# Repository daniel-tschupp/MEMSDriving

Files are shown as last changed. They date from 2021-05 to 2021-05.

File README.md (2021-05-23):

# OCT MEMS Scanhead

As my second project in my master studies designed a 2d OCT MEMS Scanhead.

It contained three main tasks:
* Signal processing for drifing the MEMS
* Driver electronics design
* MCU Signal generation electronics design including Software

This repository contains the entier work including a documantaion in pdf format and the presentation as a video in german.

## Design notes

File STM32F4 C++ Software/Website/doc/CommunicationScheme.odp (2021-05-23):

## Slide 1

USB-C

Protocoll: json

UART

WiFi: TCP Socket

Protocoll: json

UART

Html5
Websockets

Host PC

Labview serial port

C++ serial port

Scanner PCB

FTDI

MCU

Host PC

Labview tcp-socket

C++ tcp-socket

Website

Proxy
Server

Scanner PCB

ESP8266
server
(Port:5001)

MCU

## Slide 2

Scheduler (FIFO)

Taskqueue possible entries:

Initialize system on startup

USB Task:
- Check command
- Check parameter ranges
- Configure system accordingly

Wifi Task:
- Check command
- Check parameter ranges
- Configure system accordingly

Realtime (Interrupts: asynchronous)

USB-USART:
Add character to USB buffer

ESP8266-USART:
Add character to Wifi buffer

Timer DAC: (sampling frequency)
Calculate and Update
DAC value

A-Scan-Trigger:
Count A-Scans

Timer Regular checks: (100ms)
Add USB task to tasklist
Add Wifi task to tasklist

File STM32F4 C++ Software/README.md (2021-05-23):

## Overview over Documentation:
*	[Prerequisits](#Prerequisites)
*	[Main structure](#MainStructure)
*	[Hardware](#Hardware)
*	[Signal Generation](#SignalGeneration)
*	[Communication](#Communication)

_Note: When this README.md file is displayed on GitLab, the images won't be displayed.
To see the whole file, please clone the repo and execute: "$doxygen doxyfile"
on tht cmd line. Then enter "$firefox doxygen/html/index.html" 
Make sure you met the prerequisits._
 
---

## <a name="Prerequisites">Prerequisits to work on this Project:</a>

---

For Linux:
* git
* Atollic True Studio
* CubeMX
* doxygen (Download & compile the latest version from: https://gitlab.com/pages/doxygen/tree/master )
* graphviz

For Windows:
* git
* Atollic True Studio or Keil uVision
* CubeMX
* doxygen Frontend
* graphviz that works with doxygen frontend
* cygwin with doxygen and graphviz

---

## <a name="MainStructure">Main structure of the software:</a>

---

The Software is build up into 2 parts:
* Foreground (Time critical)
* Background (still realtime but not time critical)

MEMSScanner
!
### Foreground
The foreground only consists of interrupt service routins. The main part is the signal generation for the MEMS mirrors (Timer 13). 
But there are also some timer interrupts for event generation for the background part of the software.

Actual tasks of the foreground:
*	x-axis and y-axis signal generation (timer 13)
*	a-scan trigger generation (timer 1: CH1=PWM, CH2=CountCycles)
*	SysTick (1ms)
*	Regulare 100ms Event for background

### Background
The background conserns with all the things that are not time critical. Though it should be fast enough so the user of the software doesn't notice any delays.
Actual the tasks of the background are:
*	Initialisation
*	Communication to Host
*	Protocol parsing
*	Scan initiation
*	GPIO handling

### Build up
The MEMS_Scanner object contains a minimalistic scheduler. This is achived with a Interrupt safe FIFO-Queue and Interrupts that inserts tasks into this queue. This are the typical background activities.

To check the validity of incoming messages/commands it contains an JSONChecker object.

To create new Signal it contains a SignalFactory object.

To access the hardware components of the microcontroller like GPIO, DAC, UART etc. it contains a Hardware object.

To actually write the signals to the outputs (foreground task) it contains furthermore a SigStateMachine object.

### <a name="Hardware">Hardware</a>

To access the hardware (like GPIOs etc.) there exist a class Hardware. This class contains objects for all the used hardware. This is in particular:
* GPIO Enable HV Amplifier
* GPIO Enable HV Generation
* UART - USB Communication
* DAC1 for Y axis signal creation
* DAC2 for X axis signal creation
* SPI - Bluetooth Communication (not yet implemented)

UML:

Hardware

### SignalManager
To have things well sorted inside the main MEMS_Scanner class, there exists a SignalManager object. It contains everything about the signal generation as well as the actual state, values, mode etc. of the signal generation.

UML:

SignalManager

### FIFOQueueISRsafe
As described above the microcontroller software generates Events through interrupts. Those interruptse add Tasks to this interrupt save task queue. This provides a minimal FIFO scheduler functionality which is great to add additional software components.
But for the actual generation of the Signals in a 100kHz rate it's to slow. That's why the generation of the signals is handed separately, direct in the 100kHz timer interrupt.
All the other tasks of the software that are less time critical are handled via this queue. Ath the moment this includes the following tasks:
* Communication
* JSON string checking
* JSON string parsing
* Microcontroller configuration
* Signal configuration

UML:

FIFOQueue

---

## <a name="SignalGeneration">Signal-Generation</a>

---

### <a name="StateMachine">SigStateMachine</a>
A state machine called by the interrupt of timer 13 ensures that the signal is generated correctly. The structure of this
state machine can be seen below:

IState Attribute

As can be seen, the state machine contains a member that is an interface for a state. In the following UML you can see all the classes that 
implements this interface.
IState

---

### <a name="Signal">Signal</a>

There are some common tasks that a signal must be able to perform, regardless of how its form looks like. To represent that in software a
parrent class Signal is implemented. This parrent class implements:
* Filtering the Signal if needed
* Ramp smoothly to starting position of the signal
* simulating a filtered signal to calc phase shift and damping

The next UML shows this parrent class and all it's siblings:

Signal

As can be seen, the siblings implement primarily the pure virtual calcNextValue() - method of the parrent. This method implements the different waveform calculation.

At the moment three waveforms are implemented:
* ConstantSignal
* SinSignal
* TriangleSignal

Furthermore the parrent class contains a filter interface. This is for easy implementing other filter alorithms. The UML shows how it works:

IFilter

As for now only one filter algorithm is implemented and that is a Bessel6thOrder300Hz filter with a cut of frequency of 300Hz. The filter implementation primarily implements the filter() - method. This method must be able to calculate the next filtered value out of the new theoretical value. Because the Signals need a filtering object there is also a NoFilter object with just returns the given value.

### SignalFactory

To actually create the singal object there exists a factory. The Factory includes a map that generates the correcte signal according to the string given by the json command string. Refere to the UML to see the factory methods provided:

SineFactory
TriangleFactory
ConstantFactory

---

## <a name="Communication">Communication</a>

---

The communication to the microcontroller can be via Bluetooth or USB type C connection. The USB protocoll is only USB 2.0 because of the FTDI Chip that's mountet on the print. Due to the BUS speed of the UART1 of the microcontroller a maximal data rate of about tMbits is possible.
The chosen protocol for the communication is JSON because it's user readable, easy debuggable and also well established. Furthermore it's a lightwidth protocol with a very small amount of overhead.  

### <a name="Protocol">Protocol

#### Definition of the Communication

This chapter describes all the available commands in json format.

Get actual state:

	{
		"GetState"
	}

Actual State Answer:

	{
		"ActState": {
			"OCTType": "SpectrometerOCT",		/* Options: "SpectrometerOCT", "SSOCT" */
			"DACSamplingFrequency": 100000,		/* 10k [Hz] */
			"AScanFrequency": 20000,		/* 1-120'000 [Hz]*/
			"ScanningMode": "SingleScan",		/* Options: "SingleScan", "ContinuousScan", "NotConfigured" */
			"RunningState": "Idle",			/* OneScan, "Run", "Idle" */
			"XAxisSignalType": "SineSignal",	/* Options: "SineSignal","TriangleSignal","ConstantSignal"*/
			"YAxisSignalType": "ConstantSignal",	/* Options: "SineSignal","TriangleSignal","ConstantSignal"*/		
			"AScansPerBScan": 500,			/* Range: 0-65535 */
			"BScansPerCScan": 500,			/* Range: 0-65535 */
			"ErrorState": "NoError"			/* Errors:	NoError, WrongJSON, UnknownCMD, MissingParameter, ScanModeNotConfigured, WrongParameterRange, ToManyAttributes, EmptyJSON */
		}
	}      

Configure microcontroller:

	{
		"MCUConfig": {
			"OCTType": "SpectrometerOCT",	/* Options: "SpectrometerOCT", "SSOCT" */
			"AScanFrequency": 20000,	/* 1-1'000'000 [Hz] */
			"ScanningMode": "SingleScan"	/* Options: "SingleScan", "ContinuousScan" */
		}
	}     

Configure a sine wave:

	{
		"SineSignal": { 
			"OutputStage" : "XAxis", 	/* Options: "XAxis", "YAxis" */
			"Frequency" : 120, 		/* 0.001 - 1500 [Hz] */
			"Amplitude" : 1.5,		/* 0 - 1.5 [V] */
			"Phase": 0,			/* 0-360 [deg] */
			"Offset": 0,			/* -1.5 - 1.5 [V] */
			"Filter": "NoFilter"		/* Options: 	"NoFilter", "Bessel6thOrder300Hz", "MagnMemsIIR10000", "IIR_X", "IIR_Y" */
		}
	}  

Configure a trianglular wave:

	{
		"TriangleSignal": { 
			"OutputStage" : "XAxis",	/* Options: XAxis, YAxis */
			"Frequency" : 200, 		/* 0.01 - 1000 [Hz] */
			"Amplitude" : 1.5,		/* 0 - 1.5 [V] */
			"Phase": 90,			/* 0-360 [deg] */
			"Offset": 0,			/* -1.5 - 1.5 [V] */
			"Width": 0.5,			/* 0 - 1[1] Defines stepness of slopes*/
			"Filter": "IIR_X"		/* Options: 	"NoFilter", "Bessel6thOrder300Hz", "MagnMemsIIR10000", "IIR_X", "IIR_Y" */
		}
	}

Configure a constant signal:

	{
		"ConstantSignal": { 
			"OutputStage" : "XAxis", 	/* Options: XAxis, YAxis */
			"Duration" : 0.05, 		/* 000001 - 15000 [s] */
			"DCValue" : 0,			/* -1.5 - 1.5 [V] */
			"Offset": 0,			/* -1.5 - 1.5 [V] */
			"Filter": "NoFilter"		/* Options: 	"NoFilter", "Bessel6thOrder300Hz", "MagnMemsIIR10000", "IIR_X", "IIR_Y" */
		}
	}

Sending IIR filter parameter:
	
	{
		"SetFilter": {
			"FilterName": "IIR_X",	/* Name of the Filter can be arbitrary*/
			"Fs": 10000.0,		/* Sampling frequency of filter */
			"Gain": 1.1,		/* Gain of the Filter */
			"a0": 1.0,		/* Filter coefficients */
			"a1": 1.0,
			"a2": 1.0,
			"a3": 1.0,
			"a4": 1.0,
			"b0": 1.0,
			"b1": 1.0,
			"b2": 1.0,
			"b3": 1.0,
			"b4": 1.0
		}
	}

Start Signal playing:

	{
		"RunScan"
	}

Stop Signal playing:

	{
		"StopScan"
	}

#### SimpleJSONParser

The SimpleJSONParser class provides the means to decrypt a json string and extract the sent values. For the moment this works only with easy json strings like the ones above, but not with json strings that are more nested. The underlying library of this Parser class is a super lightweith json library called jsmn. It's an open source library that can be found here: https://gitlab.com/NTPsec/ntpsec/tree/master/libjsmn

The following UMS shows the provided method:

SimpleJSONParser

#### JSONChecker

The JSONChecker class provides the means to check if a string is a json string and if it complies
to the defined syntax in the chapter protocoll. It checks the ranges of the given values too.

JSONChecker

### <a name="USB_Communication">USB_Communication</a>

The USBCom class provides methods to send strings via UART --> FTDI chip --> USB2.0.
Furthermore in combination with the UART interrupt it fills a receive buffer when characters are received. This buffer can be read via another method provided.

The following block diagram shows the communication path:
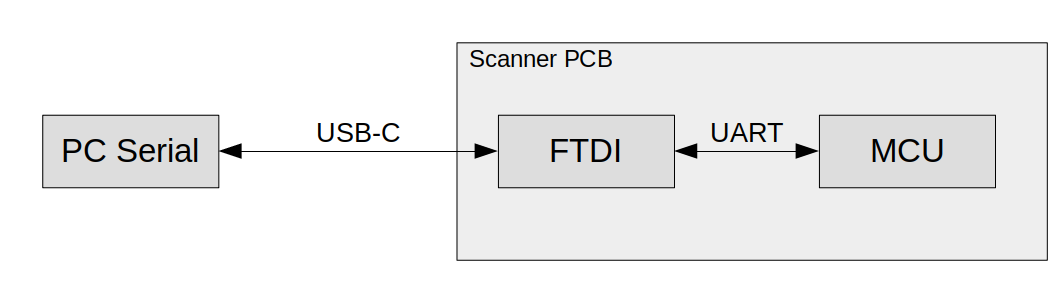
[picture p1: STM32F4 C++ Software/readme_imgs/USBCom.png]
USBCom

\image html USBCom.png

The UML shows all the provided methods: 
USBCom

### <a name="Wifi_Communication">Wifi Communication</a>

The following block diagram shows the communication path:

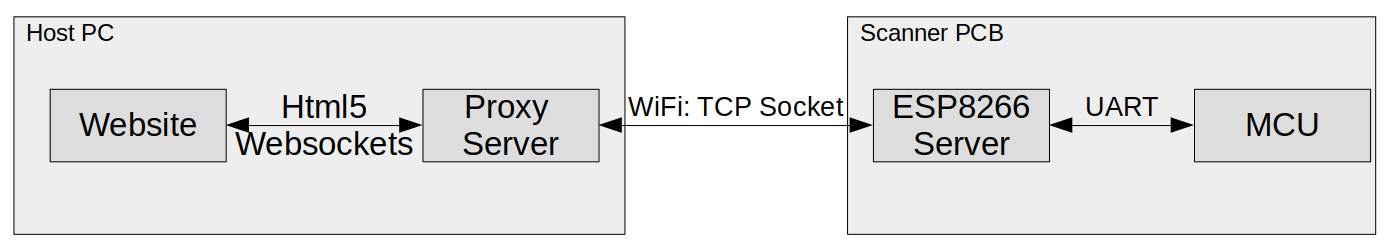
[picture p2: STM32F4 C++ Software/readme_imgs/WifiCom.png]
WifiCom

\image html WifiCom.png

The UML shows all the provided methods:
WifiCom

To use the Wifi Communication, the MCU-Print must be in the enviroment of a Network with the network ID: CompactNET and the standart optolab password.

## ESP8266 used AT commands
* ATE0 (disable Echo)
* AT+RST (reset)
* AT+CWJAP="{}OCT-Scanner","{}Optic111",1,3 (logs into a wifi access point)
* AT+CWMODE=1		(Sets esp mode to client mode only)
* AT+CIPMUX=1 (activates multiple Clients support)
* AT+CIPSERVER=1,5001		(starts server with port: 5001)
* AT+CIPSTO=6000	(sets server timeout to 6000)
* AT+CIPSEND=0,4	(sends message command, de next 4 characters will bi transmittet)
	\item MEMS				(example transmission) 
---

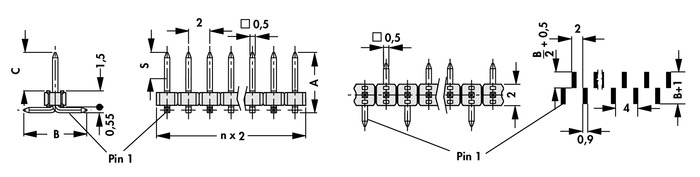
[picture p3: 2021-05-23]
Driving Electronics/Signal generator MCU circuit/datasheets/sly_7_smd_Technical_Drawing.jpg

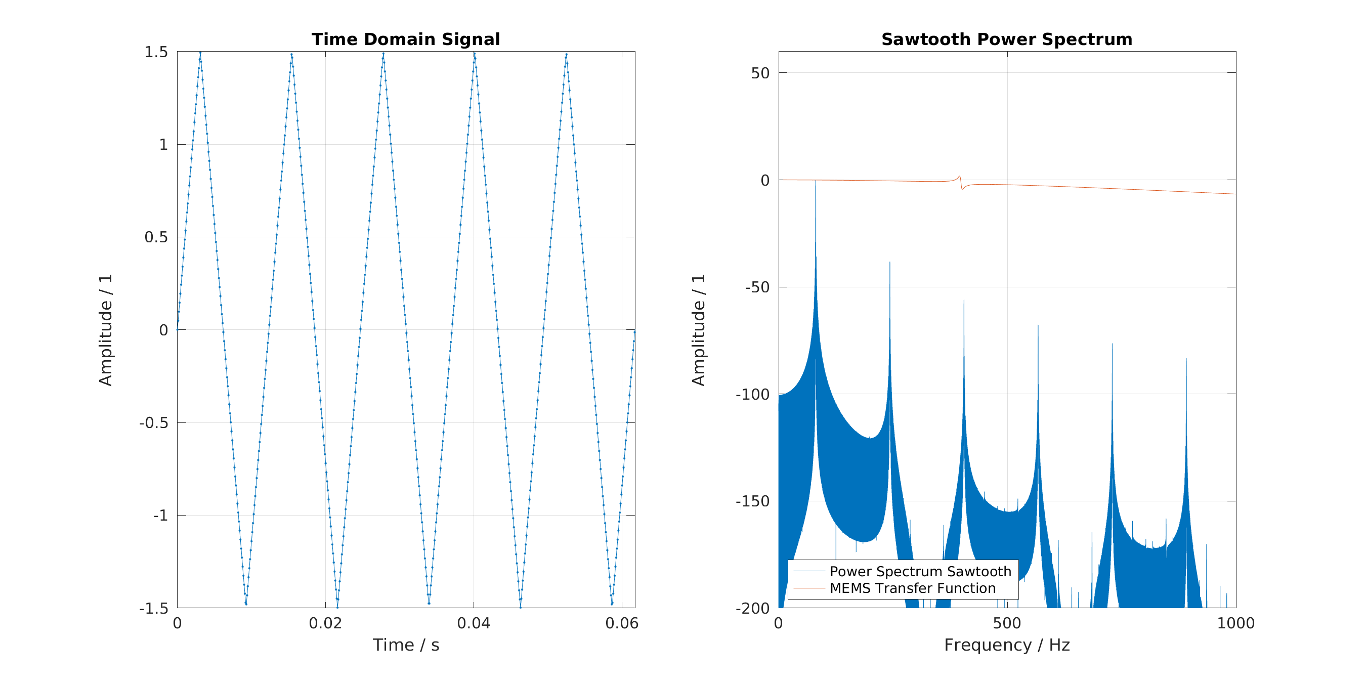
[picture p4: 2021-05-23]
Signal Generation in Matlab/Method2StateSpaceMatching/Sawtooth Power Spectrum.png

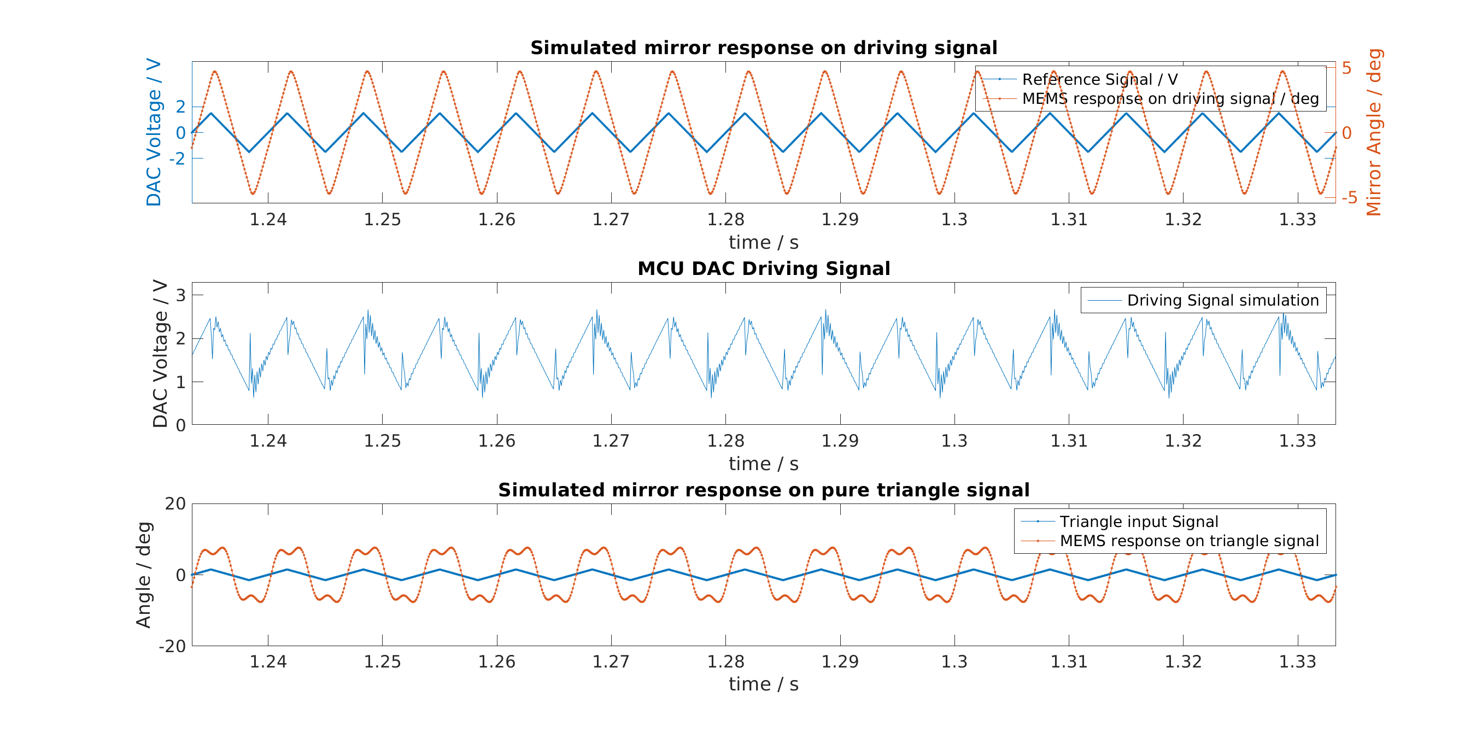
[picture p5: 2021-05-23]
Signal Generation in Matlab/Method2StateSpaceMatching/MEMS_Response.png

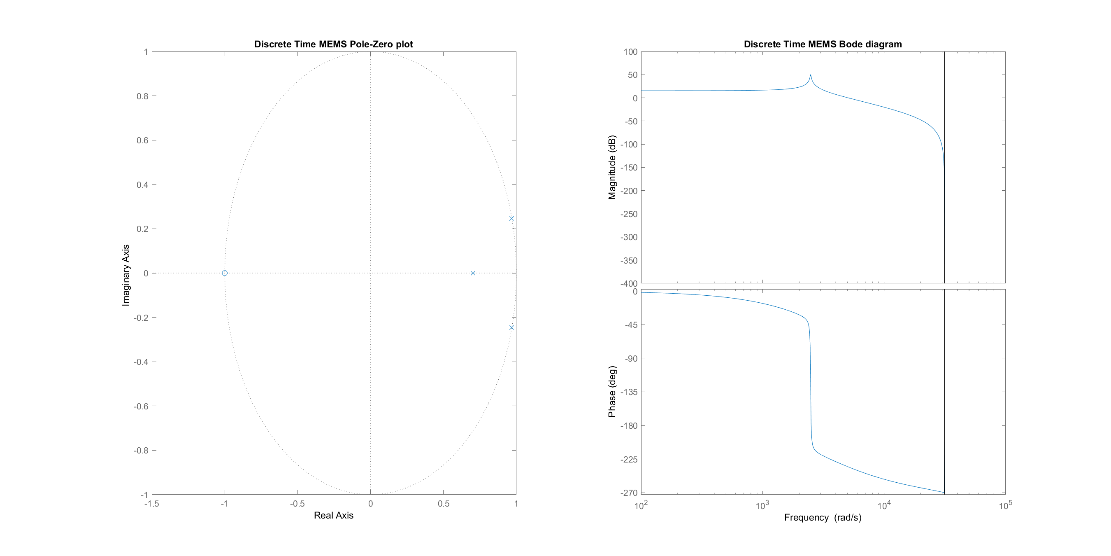
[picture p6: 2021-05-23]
Signal Generation in Matlab/Method2StateSpaceMatching/MEMS_Discrete_Bode_tustin_fs10k.png

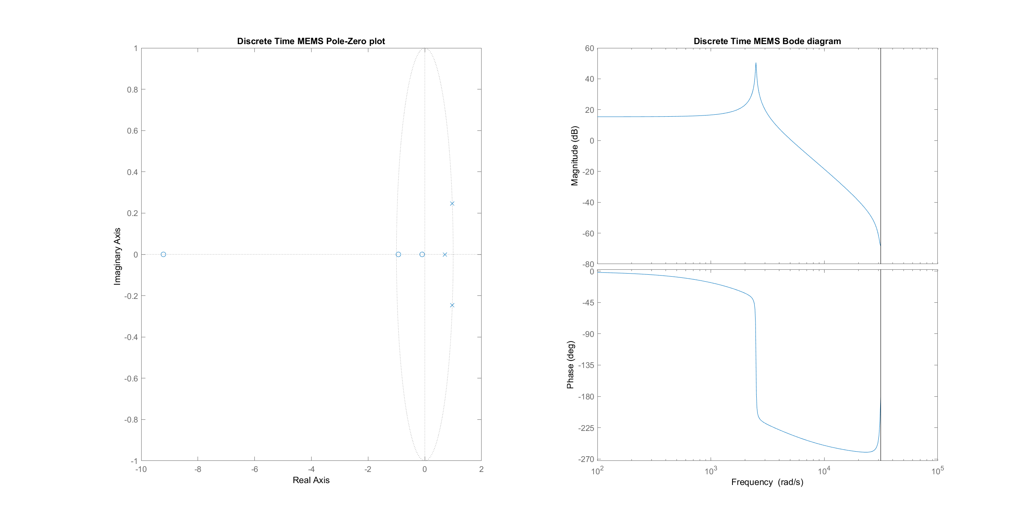
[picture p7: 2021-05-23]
Signal Generation in Matlab/Method2StateSpaceMatching/MEMS_Discrete_Bode_foh_fs10k.png

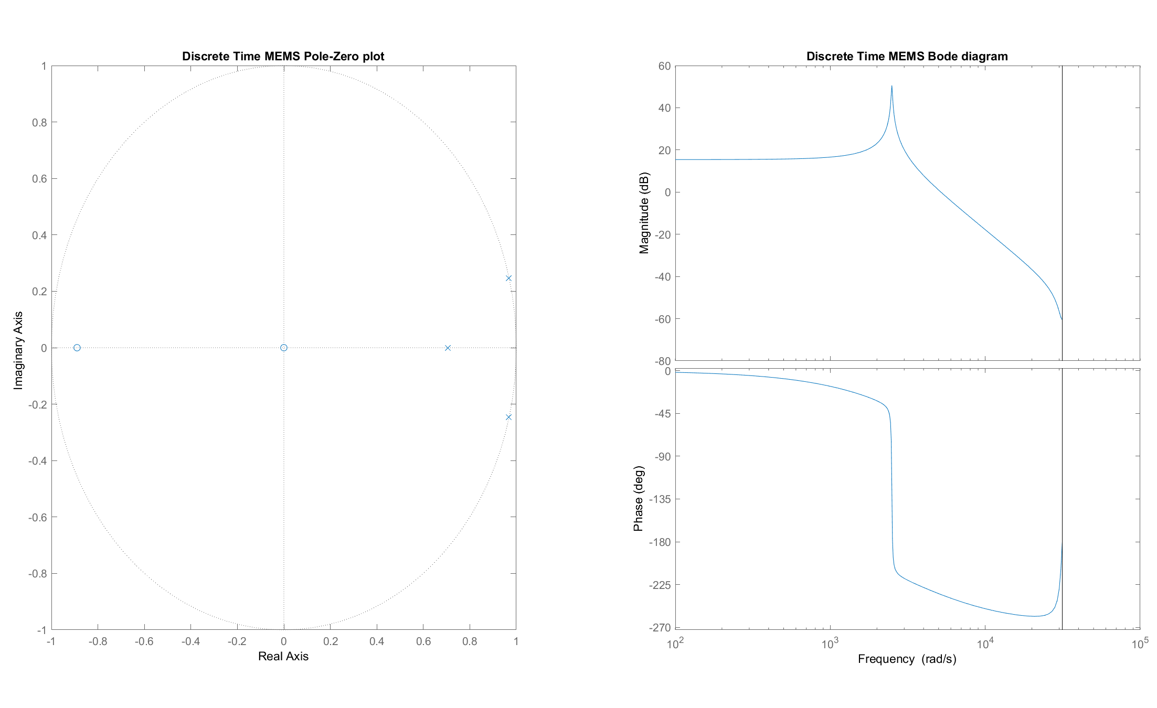
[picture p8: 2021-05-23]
Signal Generation in Matlab/Method2StateSpaceMatching/MEMS_Discrete_Bode_impulse_fs10k.png

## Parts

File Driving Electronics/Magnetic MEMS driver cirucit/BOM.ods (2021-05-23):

BOM
 | Number of Boards: | 2
Qty | Value | Device | Package | Parts | MOUSER | PREIS | Qty tot | Total CHF
Additional:
1 | Heat Sink |  |  |  | 501200B00000G | 1.63 | 2 | 3.26
4 | Picoblade 3P Stecker |  |  |  | 51021-0300 | 0.20 | 8 | 1.608
5 | Picoblade 2P Stecker |  |  |  | 51021-0200 | 0.17 | 10 | 1.74
1 | Picoblade 10P |  |  |  | 51021-1000 | 0.31 | 2 | 0.622
15 | Picoblade Kabel |  |  |  | 79758-0006 | 0.54 | 30 | 16.2
100 | Picoblade Crimp Contact |  |  |  | 50079-8000 | 0.03 | 200 | 6.4
1 | Coil Ringcore |  |  | (Farnell!) | TN9/6/3-4C65 | 0.93 | 2 | 1.866
1 | 22uF Elko |  |  |  | ECE-A1CKA220I | 0.20 | 2 | 0.402
2 | 10uF Elko |  |  |  | ECE-A1CKA100I | 0.20 | 4 | 0.804
Schema:
1 | 1.5nF | C-EUC0805K | C0805K | C1 | 0805B152K500CT | 0.117 | 2 | 0.234
1 | 100k, 1% | R-EU_R0603 | R0603 | R3 | MCT06030C1003FP500 | 0.12 | 2 | 0.24
9 | 100nF | C-EUC0603K | C0603K | C6, C7, C8, C10, C11, C12, C13, C14, C15 | 06033C104KAT4A | 0.082 | 18 | 1.476
1 | 10k | R-EU_R0603 | R0603 | R1 | ESR03EZPF62R0 | 0.147 | 2 | 0.294
1 | 110k, 1% | R-EU_R0603 | R0603 | R7 | CRCW0603110KFKEAC | 0.12 | 2 | 0.24
2 | 120k, 1% | R-EU_R0603 | R0603 | R2, R12 | MCT06030C1203FP500 | 0.092 | 4 | 0.368
1 | 150pF | C-EUC0603K | C0603K | C9 | C0603C101M5HACTU | 0.092 | 2 | 0.184
1 | 1k, 20% | SM-3T | SM-3T | R15 | SM-3TW102 | 3.06 | 2 | 6.12
3 | 1uF | C-EUC0805K | C0805K | C2, C3, C4 | 0805B105K500CT | 0.199 | 6 | 1.194
1 | 1uF | C-EUC0805K | C0805K | C5 | 0805B105K500CT |  | 2 | 0
1 | 20k, 20% | SM-3T | SM-3T | R4 | SM-3TW203 | 3.06 | 2 | 6.12
1 | 360 | R-EU_R0603 | R0603 | R9 | MR06X3600FTL | 0.12 | 2 | 0.24
1 | 4.3k, 1% | R-EU_R0603 | R0603 | R14 | SDR03EZPF4301 | 0.129 | 2 | 0.258
1 | 4.9k, 1% | R-EU_R0603 | R0603 | R16 | MCT0603MC4701FP500 | 0.092 | 2 | 0.184
1 | 51k, 1% | R-EU_R0603 | R0603 | R13 | MCT06030C5102FP500 | 0.137 | 2 | 0.274
1 | 51k, 1% | R-EU_R0603 | R0603 | R17 | MCT06030C5102FP500 | 0.137 | 2 | 0.274
1 | 52745-0690 | 52745-0690 | 52745-0690 | X12 | 52745-0697 | 0.796 | 2 | 1.592
4 | 53261-0271_2P_H | 53261-0271_2P_H | 53261-02 | J1, J2, J3, J4 | 538-53261-0271 | 0.84 | 8 | 6.72
2 | 53261-03 | 53261-03 | 53261-03 | X5, X6 | 53261-0371 | 0.52 | 4 | 2.08
1 | 53261-03 | 53261-03 | 53261-03 | X7 | 53261-0371 | 0.52 | 2 | 1.04
3 | 62, 1% | R-EU_R0603 | R0603 | R5, R6, R8 | ESR03EZPF62R0 | 0.119 | 6 | 0.714
2 | 7.5, 1%, 1/2W | R-EU_R0805 | R0805 | R10, R11 | ESR10EZPF7R50 | 0.147 | 4 | 0.588
2 | HOLES_2_7_NP | HOLES_2_7_NP | 2_7_NP | H1, H2 |  |  | 4 | 0
1 | IRF7309 | IRF7309 | SO08-IRF | KF1 | 942-IRF7309TRPBF | 0.667 | 2 | 1.334
2 | LM7341 | LM7341 | SOT23-5 | T3, T4 | 926-LM7341MF/NOPB | 2.37 | 4 | 9.48
1 | LOC110P | LOC110P | LOC110P | KF2 |  | 2.41 | 2 | 4.82
4 | M50-3 | M50-3 | M50-3 | X1, X2, X3, X4 | M50-3030342 | 0.558 | 8 | 4.464
4 | M50-3 | M50-3 | M50-3 | X8, X9, X10, X11 | M50-3530342 | 0.137 | 8 | 1.096
1 | MC78M08 | MC78M08 | DPAK-3 | G2 | MC78M08CDTG | 0.375 | 2 | 0.75
1 | MC79M08 | MC79M08 | DPAK-3 | G3 | MC79M08CDTG | 0.503 | 2 | 1.006
1 | MOUNT-HOLE2.8 | MOUNT-HOLE2.8 | 2,8 | H3 |  |  | 2 | 0
4 | OPA187 | OPA187 | SOT23-5 | T1, T2, T5, T6 | 595-OPA187IDBVR | 2.06 | 8 | 16.48
1 | RS6-0512D | RS6-0512D | RS_THT | G1 | 919-RS6-0512D | 13.92 | 2 | 27.84
10 | TP10 | TP10 | TP10 | TP1, TP2, TP3, TP4, TP5, TP6, TP7, TP8, TP9, TP10 |  |  | 20 | 0
 |  |  |  |  |  | Total: |  | 86.286

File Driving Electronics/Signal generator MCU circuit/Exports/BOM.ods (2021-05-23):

Part | Value | Device | Package | Description | DIGI-KEY | DISTRELEC | DRIVE-LEVEL | EFFICIENCY | ESR | FARNELL | MANUFACTURER | MOUSER | NUMBER-OF-ADC-CHANNELS | NUMBER-OF-CHANNELS | NUMBER-OF-IOS | NUMBER-OF-OUT | NUMBER-OF-TIMERS-COUNTERS | NUMBER_CONTACT | NUMBER_OF_POSITION | NUMBER_OF_ROW | NUMBER_PORT | OPERATING-FORCE | OPERATING-SUPPLY-VOLTAGE | OPERATING-TEMPERATURE | OPERATING-TEMPERATURE-RANG | OPERATING-TEMPERATURE-RANGE
C1 | 10NF_16V | 10NF_16V | C0603 | Multilayer ceramic capacitor SMD, 10nF ±10%, 16VDC, X7R, Kemet, Case 0603, Mouser: 80-C0603C103K4RACTM |  |  |  |  |  |  | Kemet | 80-C0603C103K4RACTM
C2 | 100NF | 100NF | C0402 | Ceramic capacitor SMD 100nF ±5%, 16VDC, X7R, Kemet, Case 0402, C0402C104J4RACTU, MLCC, Mouser: 80-C0402C104J4R |  |  |  |  |  | 2429353 | Kemet | 80-C0402C104J4R |  |  |  |  |  |  |  |  |  |  |  |  |  | -55...+125 °C
C3 | 100NF | 100NF | C0402 | Ceramic capacitor SMD 100nF ±5%, 16VDC, X7R, Kemet, Case 0402, C0402C104J4RACTU, MLCC, Mouser: 80-C0402C104J4R |  |  |  |  |  | 2429353 | Kemet | 80-C0402C104J4R |  |  |  |  |  |  |  |  |  |  |  |  |  | -55...+125 °C
C4 | 10UF_10V | 10UF_10V | C0603 | Ceramic capacitor SMD 10uF ±10%, 10VDC, X5R, TDK , Case 0603, Mouser: 810-C1608X5R1A106K | 445-7486-1-ND |  |  |  |  | 2211164 | TDK | 810-C1608X5R1A106K
C6 | 4,7UF_16V | 4,7UF_16V | C0603 | Multilayer Ceramic Capacitors MLCC, SMD 4,7uF ±10%, 16VDC, X5R, YAGEO , Case 0603, Mouser: 603-CC603KRX5R7BB475 | 311-1785-2-ND |  |  |  |  |  | Yageo | 603-CC603KRX5R7BB475
C7 | 100NF | 100NF | C0402 | Ceramic capacitor SMD 100nF ±5%, 16VDC, X7R, Kemet, Case 0402, C0402C104J4RACTU, MLCC, Mouser: 80-C0402C104J4R |  |  |  |  |  | 2429353 | Kemet | 80-C0402C104J4R |  |  |  |  |  |  |  |  |  |  |  |  |  | -55...+125 °C
C8 | 100NF | 100NF | C0402 | Ceramic capacitor SMD 100nF ±5%, 16VDC, X7R, Kemet, Case 0402, C0402C104J4RACTU, MLCC, Mouser: 80-C0402C104J4R |  |  |  |  |  | 2429353 | Kemet | 80-C0402C104J4R |  |  |  |  |  |  |  |  |  |  |  |  |  | -55...+125 °C
C9 | 100NF | 100NF | C0402 | Ceramic capacitor SMD 100nF ±5%, 16VDC, X7R, Kemet, Case 0402, C0402C104J4RACTU, MLCC, Mouser: 80-C0402C104J4R |  |  |  |  |  | 2429353 | Kemet | 80-C0402C104J4R |  |  |  |  |  |  |  |  |  |  |  |  |  | -55...+125 °C
C10 | 10UF_10V | 10UF_10V | C0603 | Ceramic capacitor SMD 10uF ±10%, 10VDC, X5R, TDK , Case 0603, Mouser: 810-C1608X5R1A106K | 445-7486-1-ND |  |  |  |  | 2211164 | TDK | 810-C1608X5R1A106K
C11 | 100NF | 100NF | C0402 | Ceramic capacitor SMD 100nF ±5%, 16VDC, X7R, Kemet, Case 0402, C0402C104J4RACTU, MLCC, Mouser: 80-C0402C104J4R |  |  |  |  |  | 2429353 | Kemet | 80-C0402C104J4R |  |  |  |  |  |  |  |  |  |  |  |  |  | -55...+125 °C
C12 | 100NF | 100NF | C0402 | Ceramic capacitor SMD 100nF ±5%, 16VDC, X7R, Kemet, Case 0402, C0402C104J4RACTU, MLCC, Mouser: 80-C0402C104J4R |  |  |  |  |  | 2429353 | Kemet | 80-C0402C104J4R |  |  |  |  |  |  |  |  |  |  |  |  |  | -55...+125 °C
C13 | 100NF | 100NF | C0402 | Ceramic capacitor SMD 100nF ±5%, 16VDC, X7R, Kemet, Case 0402, C0402C104J4RACTU, MLCC, Mouser: 80-C0402C104J4R |  |  |  |  |  | 2429353 | Kemet | 80-C0402C104J4R |  |  |  |  |  |  |  |  |  |  |  |  |  | -55...+125 °C
C14 | 10UF_10V | 10UF_10V | C0603 | Ceramic capacitor SMD 10uF ±10%, 10VDC, X5R, TDK , Case 0603, Mouser: 810-C1608X5R1A106K | 445-7486-1-ND |  |  |  |  | 2211164 | TDK | 810-C1608X5R1A106K
C15 | 100NF | 100NF | C0402 | Ceramic capacitor SMD 100nF ±5%, 16VDC, X7R, Kemet, Case 0402, C0402C104J4RACTU, MLCC, Mouser: 80-C0402C104J4R |  |  |  |  |  | 2429353 | Kemet | 80-C0402C104J4R |  |  |  |  |  |  |  |  |  |  |  |  |  | -55...+125 °C
C16 | 2,2UF/6V3 | 2,2UF/6V3 | C0402 | Multilayer Ceramic Capacitors MLCC, SMD, 2,2uF ±10%, 6,3VDC, X5R, Kemet, Case 0402, Mouser: 80-C0402C225K9P |  | 110-95-530 |  |  |  | 2442787 | Kemet | 80-C0402C225K9P |  |  |  |  |  |  |  |  |  |  |  |  |  | -55...+85 °C
C17 | 2,2UF/6V3 | 2,2UF/6V3 | C0402 | Multilayer Ceramic Capacitors MLCC, SMD, 2,2uF ±10%, 6,3VDC, X5R, Kemet, Case 0402, Mouser: 80-C0402C225K9P |  | 110-95-530 |  |  |  | 2442787 | Kemet | 80-C0402C225K9P |  |  |  |  |  |  |  |  |  |  |  |  |  | -55...+85 °C
C18 | 15PF | 15PF | C0402 | Multilayer Ceramic Capacitors MLCC, SMD, 15pF, ±5%, 50VDC, COG, Kemet, Case 0402, Mouser: 80-C0402C150J5G | 399-1014-1-ND |  |  |  |  | 1414577 | Kemet | 80-C0402C150J5G |  |  |  |  |  |  |  |  |  |  |  |  |  | -55...+125 °C
C19 | 15PF | 15PF | C0402 | Multilayer Ceramic Capacitors MLCC, SMD, 15pF, ±5%, 50VDC, COG, Kemet, Case 0402, Mouser: 80-C0402C150J5G | 399-1014-1-ND |  |  |  |  | 1414577 | Kemet | 80-C0402C150J5G |  |  |  |  |  |  |  |  |  |  |  |  |  | -55...+125 °C
C20 | 100NF | 100NF | C0402 | Ceramic capacitor SMD 100nF ±5%, 16VDC, X7R, Kemet, Case 0402, C0402C104J4RACTU, MLCC, Mouser: 80-C0402C104J4R |  |  |  |  |  | 2429353 | Kemet | 80-C0402C104J4R |  |  |  |  |  |  |  |  |  |  |  |  |  | -55...+125 °C
C21 | 100NF | 100NF | C0402 | Ceramic capacitor SMD 100nF ±5%, 16VDC, X7R, Kemet, Case 0402, C0402C104J4RACTU, MLCC, Mouser: 80-C0402C104J4R |  |  |  |  |  | 2429353 | Kemet | 80-C0402C104J4R |  |  |  |  |  |  |  |  |  |  |  |  |  | -55...+125 °C
C22 | 10UF_10V | 10UF_10V | C0603 | Ceramic capacitor SMD 10uF ±10%, 10VDC, X5R, TDK , Case 0603, Mouser: 810-C1608X5R1A106K | 445-7486-1-ND |  |  |  |  | 2211164 | TDK | 810-C1608X5R1A106K
C23 | 100NF | 100NF | C0402 | Ceramic capacitor SMD 100nF ±5%, 16VDC, X7R, Kemet, Case 0402, C0402C104J4RACTU, MLCC, Mouser: 80-C0402C104J4R |  |  |  |  |  | 2429353 | Kemet | 80-C0402C104J4R |  |  |  |  |  |  |  |  |  |  |  |  |  | -55...+125 °C
C24 | 100NF | 100NF | C0402 | Ceramic capacitor SMD 100nF ±5%, 16VDC, X7R, Kemet, Case 0402, C0402C104J4RACTU, MLCC, Mouser: 80-C0402C104J4R |  |  |  |  |  | 2429353 | Kemet | 80-C0402C104J4R |  |  |  |  |  |  |  |  |  |  |  |  |  | -55...+125 °C
C25 | 10UF_10V | 10UF_10V | C0603 | Ceramic capacitor SMD 10uF ±10%, 10VDC, X5R, TDK , Case 0603, Mouser: 810-C1608X5R1A106K | 445-7486-1-ND |  |  |  |  | 2211164 | TDK | 810-C1608X5R1A106K
C26 | 10UF_10V | 10UF_10V | C0603 | Ceramic capacitor SMD 10uF ±10%, 10VDC, X5R, TDK , Case 0603, Mouser: 810-C1608X5R1A106K | 445-7486-1-ND |  |  |  |  | 2211164 | TDK | 810-C1608X5R1A106K
D1 | ZEN056V115A24LS | ZEN056V115A24LS | 1616_LS | Polizen, Polymer Enhanced Zener Diode, 5,6V, PPTC/Zener SMD, Littelfuse, Mouser : 650-ZEN056V115A24LS | ZEN056V115A24LSCT-ND |  |  |  |  |  | Littelfuse | 650-ZEN056V115A24LS
H1 | HOLES_2_7_NP | HOLES_2_7_NP | 2_7_NP | Hole D = 2,7mm
H2 | HOLES_2_7_NP | HOLES_2_7_NP | 2_7_NP | Hole D = 2,7mm
H3 | HOLES_2_7_NP | HOLES_2_7_NP | 2_7_NP | Hole D = 2,7mm
H4 | HOLES_2_7_NP | HOLES_2_7_NP | 2_7_NP | Hole D = 2,7mm
IC1 | STM32F405RGT6 | STM32F405RGT6 | LQFP-64 | ARM Microcontrollers - MCU ARM M4 1024 FLASH 168 Mhz 192kB SRAM, STMicroelectronics, LQFP64, STM32F405RGT6, Mouser : 511-STM32F405RGT6 |  |  |  |  |  | 2064363 |  |  | 16 |  | 51 I/O |  | 10 Timer |  |  |  |  |  | 1.8 V to 3.6 V |  |  | -40°C ~ 85°C (TA)
IC2 | LMZM23601V3SILT | LMZM23601V3SILT | USIP-10 | Non-Isolated DC/DC Converters, IN 4...36V, UOT+3,3VDC / 1A, Step-Down DC-DC Power Module in 3.8-mm x 3-mm, Package 10-uSiP,Texas Instruments, Mouser : 595-LMZM23601V3SILT | 296-49461-1-ND |  |  | 81% |  |  | Texas Instruments | 595-LMZM23601V3SILT |  |  |  | 1 |  |  |  |  |  |  |  |  |  | -40 °C ~ 125 °C
IC3 | FT232RQ | FT232RQ | QFN32 | USB Interface IC USB to Serial UART, Mouser : 895-FT232RQ (case 32-QFN) & Mouser : 895-FT232RL (case 28-SSOP) | 768-1008-1-ND |  |  |  |  | 1146033 | FTDI | 895-FT232RQ
J1 | DX07S024XJ1R1100 | DX07S024XJ1R1100 | USB-TYPE_C_JAE | USB connector HYBRID, SMD/THRU hole STD MNT, USB type C, Receptacle, female, 24 Contact, JAE Electronics, Mouser : 656-DX07S024SJ1R1100 | 670-2848-1-ND |  |  |  |  |  | JAE Electronics | 656-DX07S024SJ1R1100 |  |  |  |  |  | 24 |  |  | 1 |  |  | -30°C ~ 80°C
J2 | 53398-0271_2P_V | 53398-0271_2P_V | 53398-02 | Pin header, PicoBlade 2-pin SMD, 53398-0271, Molex, single row straight, Distrelec : 143-54-189 |  | 143-54-189 |  |  |  |  | Molex | 538-53398-0271
J3 | M50-3530342 | M50-3530342 | M50-3530342 | Single row 1.27 mm, 3 pin's, Straight solder tail, Square pin diam. 0.4 mm, Mouser : 855-M50-3530342 | 952-3599-ND |  |  |  |  |  | Harwin | 855-M50-3530342 |  |  |  |  |  |  | 3 | 1 |  |  |  | -40 °C ~ 105 °C
J4 | RECE-20449-001E-01 | RECE-20449-001E-01 | IPEX_MHF4 | RF Connectors / Coaxial Connectors Onboard Receptacle IPEX MHF4, straight, SMD, Jack, Mouser : 960-RECE20449-001E01 | 931-1158-2-ND |  |  |  |  |  |  | 960-RECE20449-001E01
J5 | RECE-20449-001E-01 | RECE-20449-001E-01 | IPEX_MHF4 | RF Connectors / Coaxial Connectors Onboard Receptacle IPEX MHF4, straight, SMD, Jack, Mouser : 960-RECE20449-001E01 | 931-1158-2-ND |  |  |  |  |  |  | 960-RECE20449-001E01
J6 | 53261-0671_6P_H | 53261-0671_6P_H | 53261-06 | Pin header, PicoBlade 6-pin SMD, 53261-0671, Molex, single row 90°, Distrelec : 143-54-312 |  |  |  |  |  |  | Molex | 538-53261-0671
J7 | 53261-7010_10P_H | 53261-7010_10P_H | 53261-10 | Pin header, PicoBlade 6-pin SMD, 53261-0671, Molex, single row 90°, Distrelec : 143-54-312 |  |  |  |  |  |  |  | 538-53261-7010
L1 | MI0805K400R-10 | MI0805K400R-10 | F0805 | Ferrite Beads 40ohms, 100MHz, 1.5A, Monolithic, case 0805, Mouser : 875-MI0805K400R-10 | 240-2389-1-ND |  |  |  |  | 2292459 | Laird | 875-MI0805K400R-10 |  |  |  |  |  |  |  |  |  |  |  | -40°C ~ 125°C
L2 | MI0805K400R-10 | MI0805K400R-10 | F0805 | Ferrite Beads 40ohms, 100MHz, 1.5A, Monolithic, case 0805, Mouser : 875-MI0805K400R-10 | 240-2389-1-ND |  |  |  |  | 2292459 | Laird | 875-MI0805K400R-10 |  |  |  |  |  |  |  |  |  |  |  | -40°C ~ 125°C
LED1 | HSMQ-C190 | HSMQ-C190 | CHIP-LED-0603 | SMD LED Green, HSMQ-C190, Broadcom Limited, Package 0603, Light colour green, Mouser : 630-HSMQ-C190 |  |  |  |  |  | 2917791 | Broadcom Limited | 630-HSMQ-C190 |  |  |  |  |  |  |  |  |  |  |  |  | -40...+85 °C
LED2 | HSMR-C190 | HSMR-C190 | CHIP-LED-0603 | SMD LED blue, HSMR-C190, Broadcom Limited, Package 0603, Light colour blue, Mouser : 630-HSMR-C190 |  |  |  |  |  | 1652108 | Broadcom Limited | 630-HSMR-C190 |  |  |  |  |  |  |  |  |  |  |  |  | -40...+85 °C
LED3 | HSMR-C190 | HSMR-C190 | CHIP-LED-0603 | SMD LED blue, HSMR-C190, Broadcom Limited, Package 0603, Light colour blue, Mouser : 630-HSMR-C190 |  |  |  |  |  | 1652108 | Broadcom Limited | 630-HSMR-C190 |  |  |  |  |  |  |  |  |  |  |  |  | -40...+85 °C
OK1 | ACPL-M21L | ACPL-M21L | SO-5 | High Speed Optocouplers Optocoupler 5MBd, case SO-5, Avago, Mouser : 630-ACPL-M21L-500E |  |  |  |  |  | 2213628 | Broadcom Limited | 630-ACPL-M21L-500E |  | 1 |  |  |  |  |  |  |  |  |  | -40°C ~ 105°C
Q1 | CX5032GA08000H0PST02 | CX5032GA08000H0PST02 | CX5032GA | SMD Crystals, 8MHz, 12pF, 50ppm, Kyocera, Mouser : 581-CX5032GA08H0PST | 1253-1691-1-ND |  | 500 uW |  | 200 Ohm |  | Kyocera | 581-CX5032GA08H0PST |  |  |  |  |  |  |  |  |  |  |  | -40°C ~ 125°C
R1 | 2K | 2K | R0603 | ±Resistor SMD 2 kΩ 1 %, ERJ-3EKF2001V, Panasonic, Case 0603, Mouser : 667-ERJ-3EKF2001V |  | 300-37-855 |  |  |  |  | Panasonic | 667-ERJ-3EKF2001V
R2 | 2K | 2K | R0603 | ±Resistor SMD 2 kΩ 1 %, ERJ-3EKF2001V, Panasonic, Case 0603, Mouser : 667-ERJ-3EKF2001V |  | 300-37-855 |  |  |  |  | Panasonic | 667-ERJ-3EKF2001V
R3 | 5K1 | 5K1 | R0603 | ±Resistor SMD 5,1 kΩ, 1 %, 0,1W, ERJ-3EKF5101V, Panasonic, Case 0603, Mouser : 667-ERJ-3EKF5101V |  | 300-37-965 |  |  |  | 2059378 | Panasonic | 667-ERJ-3EKF5101V
R4 | 5K1 | 5K1 | R0603 | ±Resistor SMD 5,1 kΩ, 1 %, 0,1W, ERJ-3EKF5101V, Panasonic, Case 0603, Mouser : 667-ERJ-3EKF5101V |  | 300-37-965 |  |  |  | 2059378 | Panasonic | 667-ERJ-3EKF5101V
R5 | 24E | 24E | R0402 | ±Resistor SMD 24Ω, 1 %, 100mW 50V, ERJ-2RKF24R0X, Panasonic, Case 0402, Mouser : 667-ERJ-2RKF24R0X |  |  |  |  |  | 2302458 | Panasonic | 667-ERJ-2RKF24R0X |  |  |  |  |  |  |  |  |  |  |  |  |  | - 55 C to + 155 C
R6 | 24E | 24E | R0402 | ±Resistor SMD 24Ω, 1 %, 100mW 50V, ERJ-2RKF24R0X, Panasonic, Case 0402, Mouser : 667-ERJ-2RKF24R0X |  |  |  |  |  | 2302458 | Panasonic | 667-ERJ-2RKF24R0X |  |  |  |  |  |  |  |  |  |  |  |  |  | - 55 C to + 155 C
R7 | 1K | 1K | R0603 | ±Resistor SMD 1 kΩ, 1 %, 0,1W, ERJ-3EKF1001V , Panasonic, Case 0603, Mouser : 667-ERJ-3EKF1001V | P1.00KHCT-ND |  |  |  |  |  | Panasonic | 667-ERJ-3EKF1001V
R8 | 1K3 | 1K3 | R0402 | ±Resistor SMD 1,3 kΩ 1 % 100mW 50V, ERJ-2RKF1301X, Panasonic, Case 0402, Mouser : 667-ERJ-2RKF1301X |  | 300-37-644 |  |  |  | 2059130 | Panasonic | 667-ERJ-2RKF1301X |  |  |  |  |  |  |  |  |  |  |  |  |  | - 55 C to + 155 C
R9 | 10K | 10K | R0402 | ±Resistor SMD 10KΩ, 1 %, 100mW 50V, ERJ-2RKF1002X, Panasonic, Case 0402, Mouser : 667-ERJ-2RKF1002X |  | 300-37-626 |  |  |  | 2302739 | Panasonic | 667-ERJ-2RKF1002X |  |  |  |  |  |  |  |  |  |  |  |  |  | - 55 C to + 155 C
R10 | 510E | 510E | R0402 | ±Resistor SMD 510Ω, 1 %, 100mW 50V, ERJ-2RKF5100X, Panasonic, Case 0402, Mouser : 667-ERJ-2RKF5100X |  | 300-37-749 |  |  |  | 2302602 | Panasonic | 667-ERJ-2RKF5100X |  |  |  |  |  |  |  |  |  |  |  |  |  | - 55 C to + 155 C
R11 | 330E | 330E | R0402 | ±Resistor SMD 330Ω, 1 %, 100mW 50V, ERJ-2RKF3300X, Panasonic, Case 0402, Mouser : 667-ERJ-2RKF3300X |  | 300-37-708 |  |  |  | 2302581 | Panasonic | 667-ERJ-2RKF3300X |  |  |  |  |  |  |  |  |  |  |  |  |  | - 55 C to + 155 C
R12 | 22E | 22E | R0402 | ±Resistor SMD 24Ω, 1 %, 100mW 50V, ERJ-2RKF24R0X, Panasonic, Case 0402, Mouser : 667-ERJ-2RKF24R0X |  |  |  |  |  |  | Vishey | 71-CRCW010022R0FREL |  |  |  |  |  |  |  |  |  |  |  |  |  | - 55 C to + 125 C
R13 | 10K | 10K | R0402 | ±Resistor SMD 10KΩ, 1 %, 100mW 50V, ERJ-2RKF1002X, Panasonic, Case 0402, Mouser : 667-ERJ-2RKF1002X |  | 300-37-626 |  |  |  | 2302739 | Panasonic | 667-ERJ-2RKF1002X |  |  |  |  |  |  |  |  |  |  |  |  |  | - 55 C to + 155 C
R14 | 22E | 22E | R0402 | ±Resistor SMD 24Ω, 1 %, 100mW 50V, ERJ-2RKF24R0X, Panasonic, Case 0402, Mouser : 667-ERJ-2RKF24R0X |  |  |  |  |  |  | Vishey | 71-CRCW010022R0FREL |  |  |  |  |  |  |  |  |  |  |  |  |  | - 55 C to + 125 C
R15 | 10K | 10K | R0402 | ±Resistor SMD 10KΩ, 1 %, 100mW 50V, ERJ-2RKF1002X, Panasonic, Case 0402, Mouser : 667-ERJ-2RKF1002X |  | 300-37-626 |  |  |  | 2302739 | Panasonic | 667-ERJ-2RKF1002X |  |  |  |  |  |  |  |  |  |  |  |  |  | - 55 C to + 155 C
R16 | 10K | 10K | R0402 | ±Resistor SMD 10KΩ, 1 %, 100mW 50V, ERJ-2RKF1002X, Panasonic, Case 0402, Mouser : 667-ERJ-2RKF1002X |  | 300-37-626 |  |  |  | 2302739 | Panasonic | 667-ERJ-2RKF1002X |  |  |  |  |  |  |  |  |  |  |  |  |  | - 55 C to + 155 C
R17 | 10K | 10K | R0402 | ±Resistor SMD 10KΩ, 1 %, 100mW 50V, ERJ-2RKF1002X, Panasonic, Case 0402, Mouser : 667-ERJ-2RKF1002X |  | 300-37-626 |  |  |  | 2302739 | Panasonic | 667-ERJ-2RKF1002X |  |  |  |  |  |  |  |  |  |  |  |  |  | - 55 C to + 155 C
SW1 | EVQ-P2T02M | EVQ-P2T02M | EVQ-P2T02M | Tactile Switches FLAT ACT 2.4NF 4.7x3.5x2.1mm, Panasonic, EVQ-P2T02M, Mouser : 667-EVQ-P2T02M | P11082SCT-ND |  |  |  |  | 2459541 | Panasonic | 667-EVQ-P2T02M |  |  |  |  |  |  |  |  |  | 2.4N |  |  |  | 40 C to + 85 C
WIFI1 | ESP8266 | ESP8266 | ESP8266 |  |  |  |  |  |  |  |  | 356-ESPWROOM-02D
Cable1 | Pico-10 | Picoblade |  |  |  |  |  |  |  |  | Molex | 538-15134-1003
Cable2 | Pico-10 | Picoblade |  |  |  |  |  |  |  |  | Molex | 538-15134-1003
Cable3 | 1Stk | Pico6PolBuchse |  |  |  |  |  |  |  |  | Molex | 538-51021-0600
Cable4 | 10Stk | Pico-Einsätze |  |  |  |  |  |  |  |  | Molex | 538-50079-8100

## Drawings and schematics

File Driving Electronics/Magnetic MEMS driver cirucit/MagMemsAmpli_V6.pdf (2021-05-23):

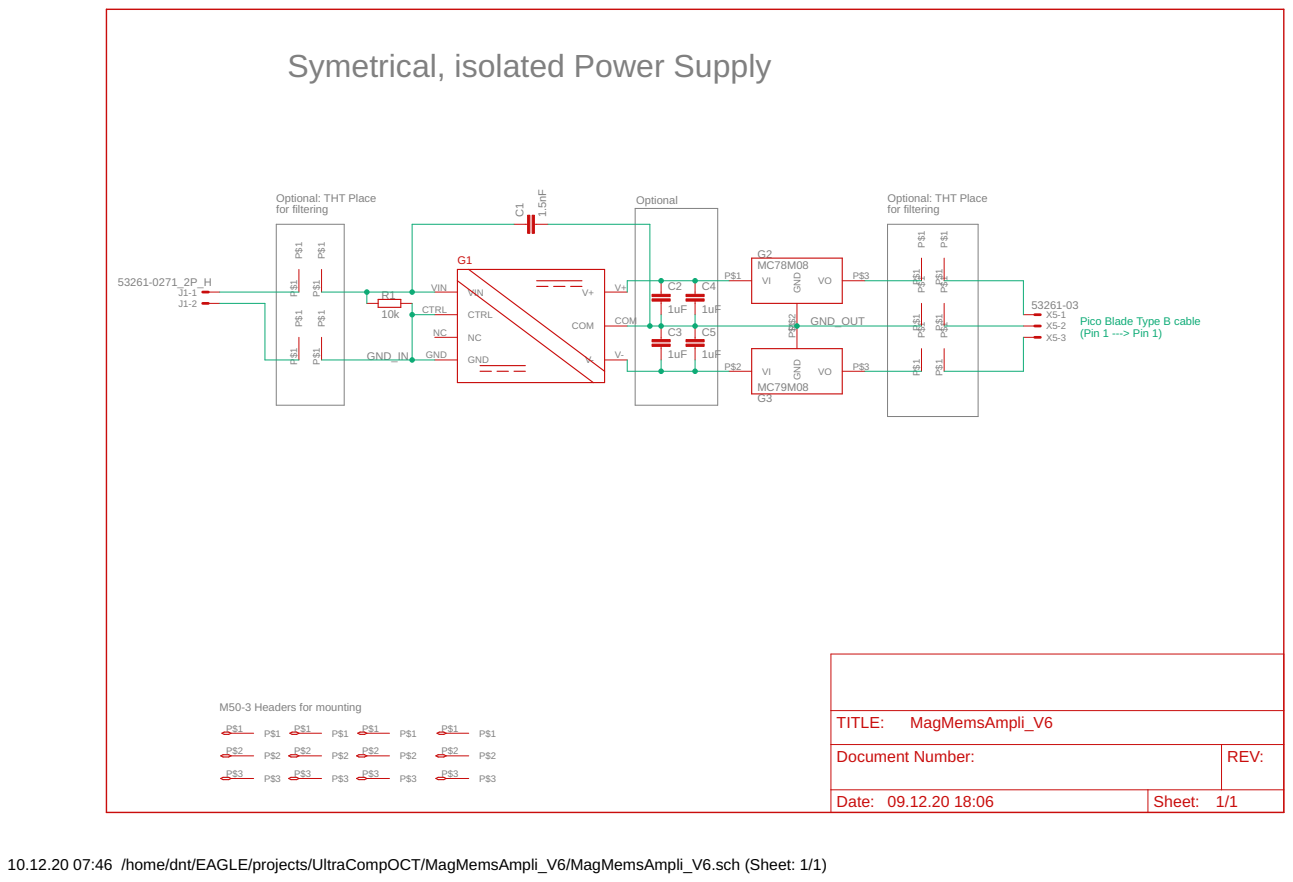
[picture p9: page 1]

Symetrical, isolated Power Supply

Pico Blade Type B cable
(Pin 1 ---> Pin 1)

Document Number: | REV:

Date: 09.12.20 18:06 | Sheet: 1/1

10.12.20 07:46 /home/dnt/EAGLE/projects/UltraCompOCT/MagMemsAmpli_V6/MagMemsAmpli_V6.sch (Sheet: 1/1)

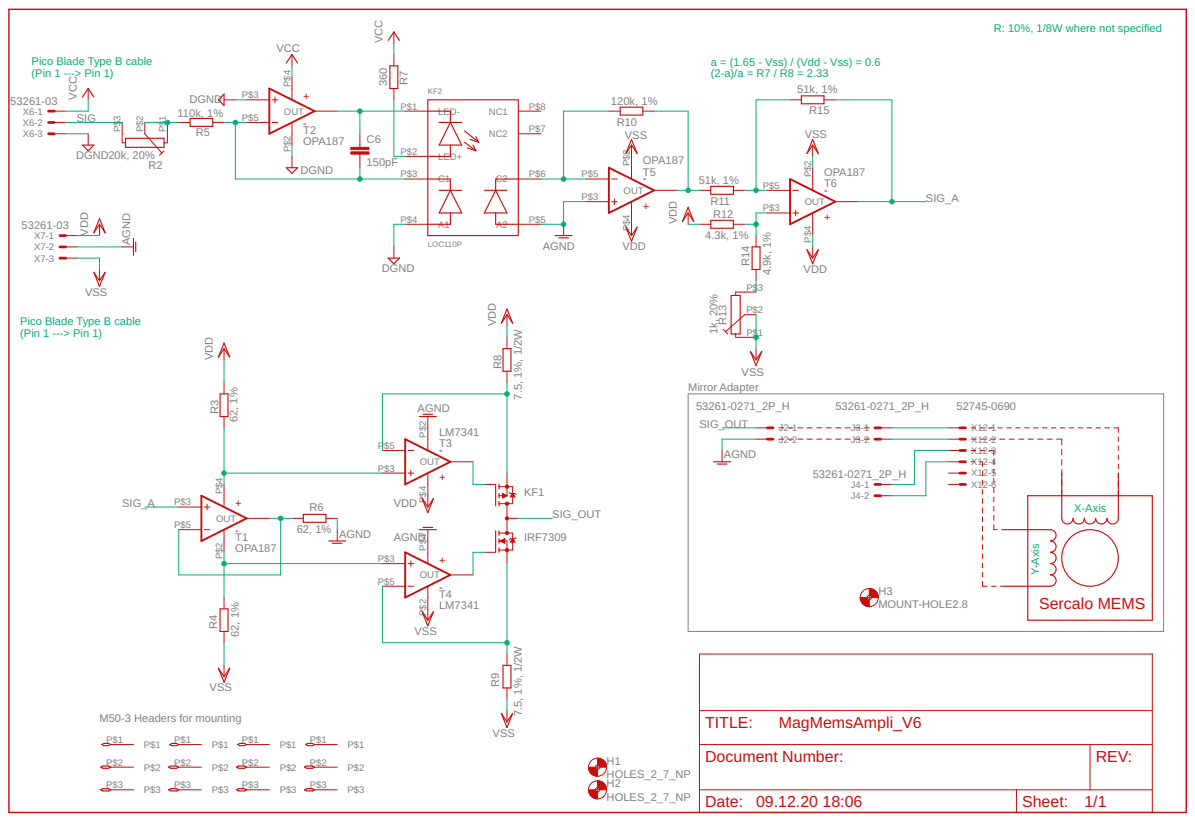
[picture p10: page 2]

X-Axis Y-Axis R: 10%, 1/8W where not specified

Pico Blade Type B cable
(Pin 1 ---> Pin 1)

Document Number: | REV:

Date: 09.12.20 18:06 | Sheet: 1/1

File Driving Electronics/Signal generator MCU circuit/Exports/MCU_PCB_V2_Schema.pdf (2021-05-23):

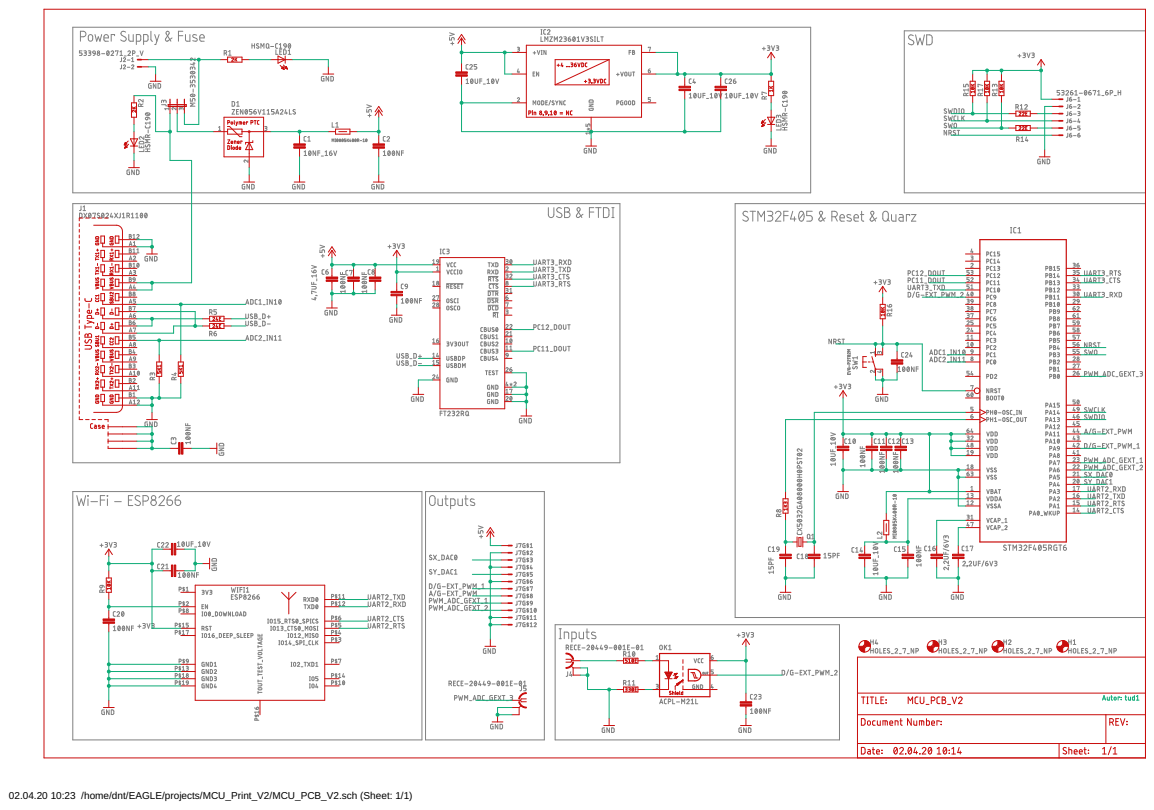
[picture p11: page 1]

02.04.20 10:23 /home/dnt/EAGLE/projects/MCU_Print_V2/MCU_PCB_V2.sch (Sheet: 1/1)

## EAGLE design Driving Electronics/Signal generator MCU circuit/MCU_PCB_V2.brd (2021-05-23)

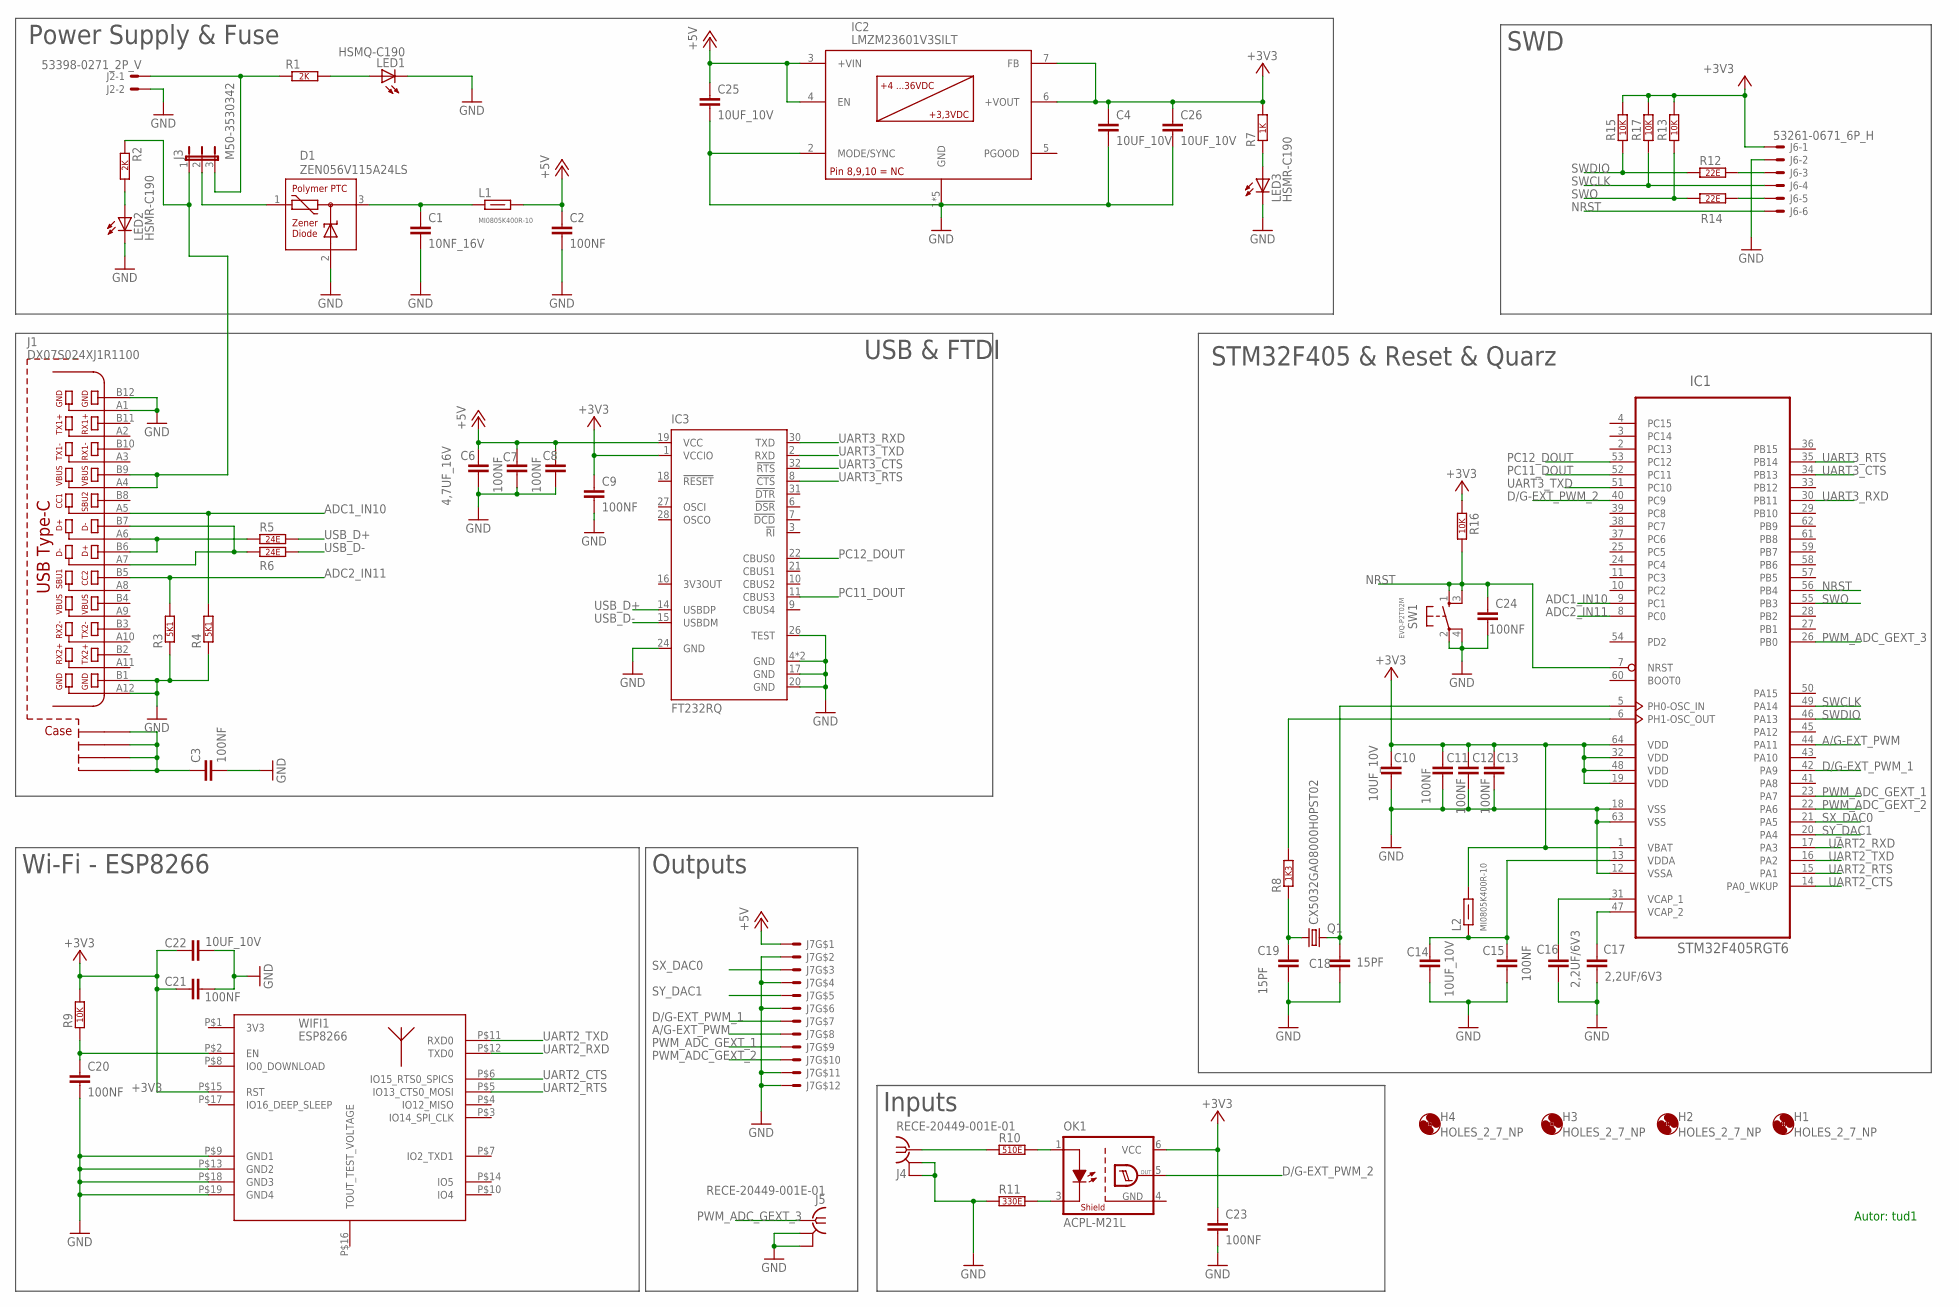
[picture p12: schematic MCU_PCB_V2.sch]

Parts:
C1: 10NF_16V; C0603
C2, C3, C7, C8, C9, C11, C12, C13, C15, C20, C21, C23, C24: 100NF; C0402
C4, C10, C14, C22, C25, C26: 10UF_10V; C0603
C6: 4,7UF_16V; C0603
C16, C17: 2,2UF/6V3; C0402
C18, C19: 15PF; C0402
D1: ZEN056V115A24LS; 1616_LS
H1, H2, H3, H4: HOLES_2_7_NP; 2_7_NP
IC1: STM32F405RGT6; LQFP-64
IC2: LMZM23601V3SILT; USIP-10
IC3: FT232RQ; QFN32
J1: DX07S024XJ1R1100; USB-TYPE_C_JAE
J2: 53398-0271_2P_V; 53398-02
J3: M50-3530342
J4, J5: RECE-20449-001E-01; IPEX_MHF4
J6: 53261-0671_6P_H; 53261-06
J7: 53261-7010_10P_H; 53261-10
L1, L2: MI0805K400R-10; F0805
LED1: HSMQ-C190; CHIP-LED-0603
LED2, LED3: HSMR-C190; CHIP-LED-0603
OK1: ACPL-M21L; SO-5
Q1: CX5032GA08000H0PST02; CX5032GA
R1, R2: 2K; R0603
R3, R4: 5K1; R0603
R5, R6: 24E; R0402
R7: 1K; R0603
R8: 1K3; R0402
R9, R13, R15, R16, R17: 10K; R0402
R10: 510E; R0402
R11: 330E; R0402
R12, R14: 22E; R0402
SW1: EVQ-P2T02M
WIFI1: ESP8266

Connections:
+3V3: C4.1, C9.1, C10.1, C11.1, C12.1, C13.1, C21.1, C22.1, C23.1, C26.1, IC1.1 (VBAT), IC1.19 (VDD), IC1.32 (VDD), IC1.48 (VDD), IC1.64 (VDD), IC2.6 (+VOUT), IC2.7 (FB), IC3.1 (VCCIO), J6.1, L2.2, OK1.6 (VCC), R7.2, R9.2, R13.2, R15.2, R16.1, R17.2, WIFI1.P$15 (RST)
+5V: C2.1, C6.1, C7.1, C8.1, C25.1, IC2.3 (+VIN), IC2.4 (EN), IC3.19 (VCC), J7.1, L1.2
A/G-EXT_PWM: IC1.44 (PA11), J7.8
ADC1_IN10: IC1.9 (PC1), J1.A5, R4.2
ADC2_IN11: IC1.8 (PC0), J1.B5, R3.2
D/G-EXT_PWM_1: IC1.42 (PA9), J7.7
D/G-EXT_PWM_2: IC1.40 (PC9), OK1.5 (OUT)
GND: C1.2, C2.2, C3.2, C4.2, C6.2, C7.2, C8.2, C9.2, C10.2, C11.2, C12.2, C13.2, C14.2, C15.2, C16.2, C17.2, C18.2, C19.2, C20.2, C21.2, C22.2, C23.2, C24.2, C25.2, C26.2, D1.2 (GND), IC1.12 (VSSA), IC1.18 (VSS), IC1.63 (VSS), IC2.1 (GND), IC2.2 (MODE/SYNC), IC2.GND@1 (GND), IC2.GND@2 (GND), IC2.GND@3 (GND), IC2.GND@4 (GND), IC3.4 (GND), IC3.17 (GND), IC3.20 (GND), IC3.24 (GND), IC3.26 (TEST), IC3.GND@3 (GND), J1.A1, J1.A12, J1.B1, J1.B12, J2.2, J4.2@1 (GND), J4.2@2 (GND), J4.NC (GND), J5.2@1 (GND), J5.2@2 (GND), J5.NC (GND), J6.2, J7.2, J7.4, J7.6, J7.S1, J7.S2, LED1.C, LED2.C, LED3.C, OK1.4 (GND), R3.1, R4.1, R11.1, SW1.2 (S), SW1.4 (S), WIFI1.P$9 (GND1), WIFI1.P$13 (GND2), WIFI1.P$18 (GND3), WIFI1.P$19 (GND4)
unnamed: J2.1, J3.3, R1.1
unnamed: LED1.A, R1.2
unnamed: D1.1 (VIN), J3.2
unnamed: C1.1, D1.3 (VOUT), L1.1
unnamed: LED2.A, R2.2
unnamed: C16.1, IC1.31 (VCAP_1)
unnamed: J1.A6, J1.B6, R5.1
unnamed: C17.1, IC1.47 (VCAP_2)
unnamed: C3.1, J1.C_FLEFT (S3), J1.C_FRIGHT (S1), J1.C_RLEFT (S4), J1.C_RRIGHT (S2)
unnamed: J1.A7, J1.B7, R6.1
unnamed: LED3.A, R7.1
unnamed: OK1.3 (C), R11.2
unnamed: C14.1, C15.1, IC1.13 (VDDA), L2.1
unnamed: C19.1, Q1.1, R8.1
unnamed: C18.1, IC1.5 (PH0-OSC_IN), Q1.2
unnamed: OK1.1 (A), R10.2
unnamed: J1.A4, J1.B9, J3.1, R2.1
unnamed: IC1.6 (PH1-OSC_OUT), R8.2
unnamed: J4.1, R10.1
unnamed: J6.3, R12.2
unnamed: J6.5, R14.2
NRST: C24.1, IC1.7 (NRST), IC1.56 (PB4), J6.6, R16.2, SW1.1, SW1.3
PC11_DOUT: IC1.52 (PC11), IC3.11 (CBUS3)
PC12_DOUT: IC1.53 (PC12), IC3.22 (CBUS0)
PWM_ADC_GEXT_1: IC1.23 (PA7), J7.9
PWM_ADC_GEXT_2: IC1.22 (PA6), J7.10
PWM_ADC_GEXT_3: IC1.26 (PB0), J5.1
SWCLK: IC1.49 (PA14), J6.4, R17.1
SWDIO: IC1.46 (PA13), R12.1, R15.1
SWO: IC1.55 (PB3), R13.1, R14.1
SX_DAC0: IC1.21 (PA5), J7.3
SY_DAC1: IC1.20 (PA4), J7.5
UART2_CTS: IC1.14 (PA0_WKUP), WIFI1.P$6 (IO15_RTS0_SPICS)
UART2_RTS: IC1.15 (PA1), WIFI1.P$5 (IO13_CTS0_MOSI)
UART2_RXD: IC1.17 (PA3), WIFI1.P$12 (TXD0)
UART2_TXD: IC1.16 (PA2), WIFI1.P$11 (RXD0)
UART3_CTS: IC1.34 (PB13), IC3.32 (!RTS)
UART3_RTS: IC1.35 (PB14), IC3.8 (!CTS)
UART3_RXD: IC1.30 (PB11), IC3.30 (TXD)
UART3_TXD: IC1.51 (PC10), IC3.2 (RXD)
USB_D+: IC3.14 (USBDP), R5.2
USB_D-: IC3.15 (USBDM), R6.2
WIFI_RST: C20.1, R9.1, WIFI1.P$2 (EN)

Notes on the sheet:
Power Supply & Fuse
USB & FTDI
SWD
STM32F405 & Reset & Quarz
Wi-Fi - ESP8266
Outputs
Inputs
Autor: tud1

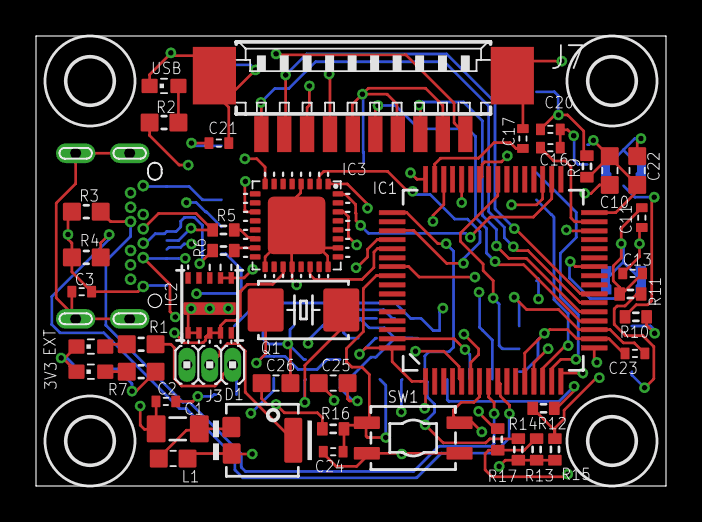
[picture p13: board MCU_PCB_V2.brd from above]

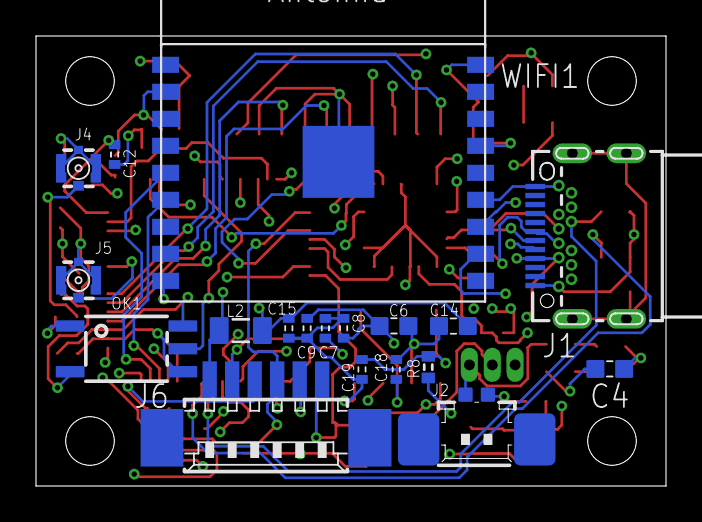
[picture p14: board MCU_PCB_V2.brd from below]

Board: 4 copper layers, 35.0 x 25.0 mm, 66 parts (19 on the bottom side), 51 nets.

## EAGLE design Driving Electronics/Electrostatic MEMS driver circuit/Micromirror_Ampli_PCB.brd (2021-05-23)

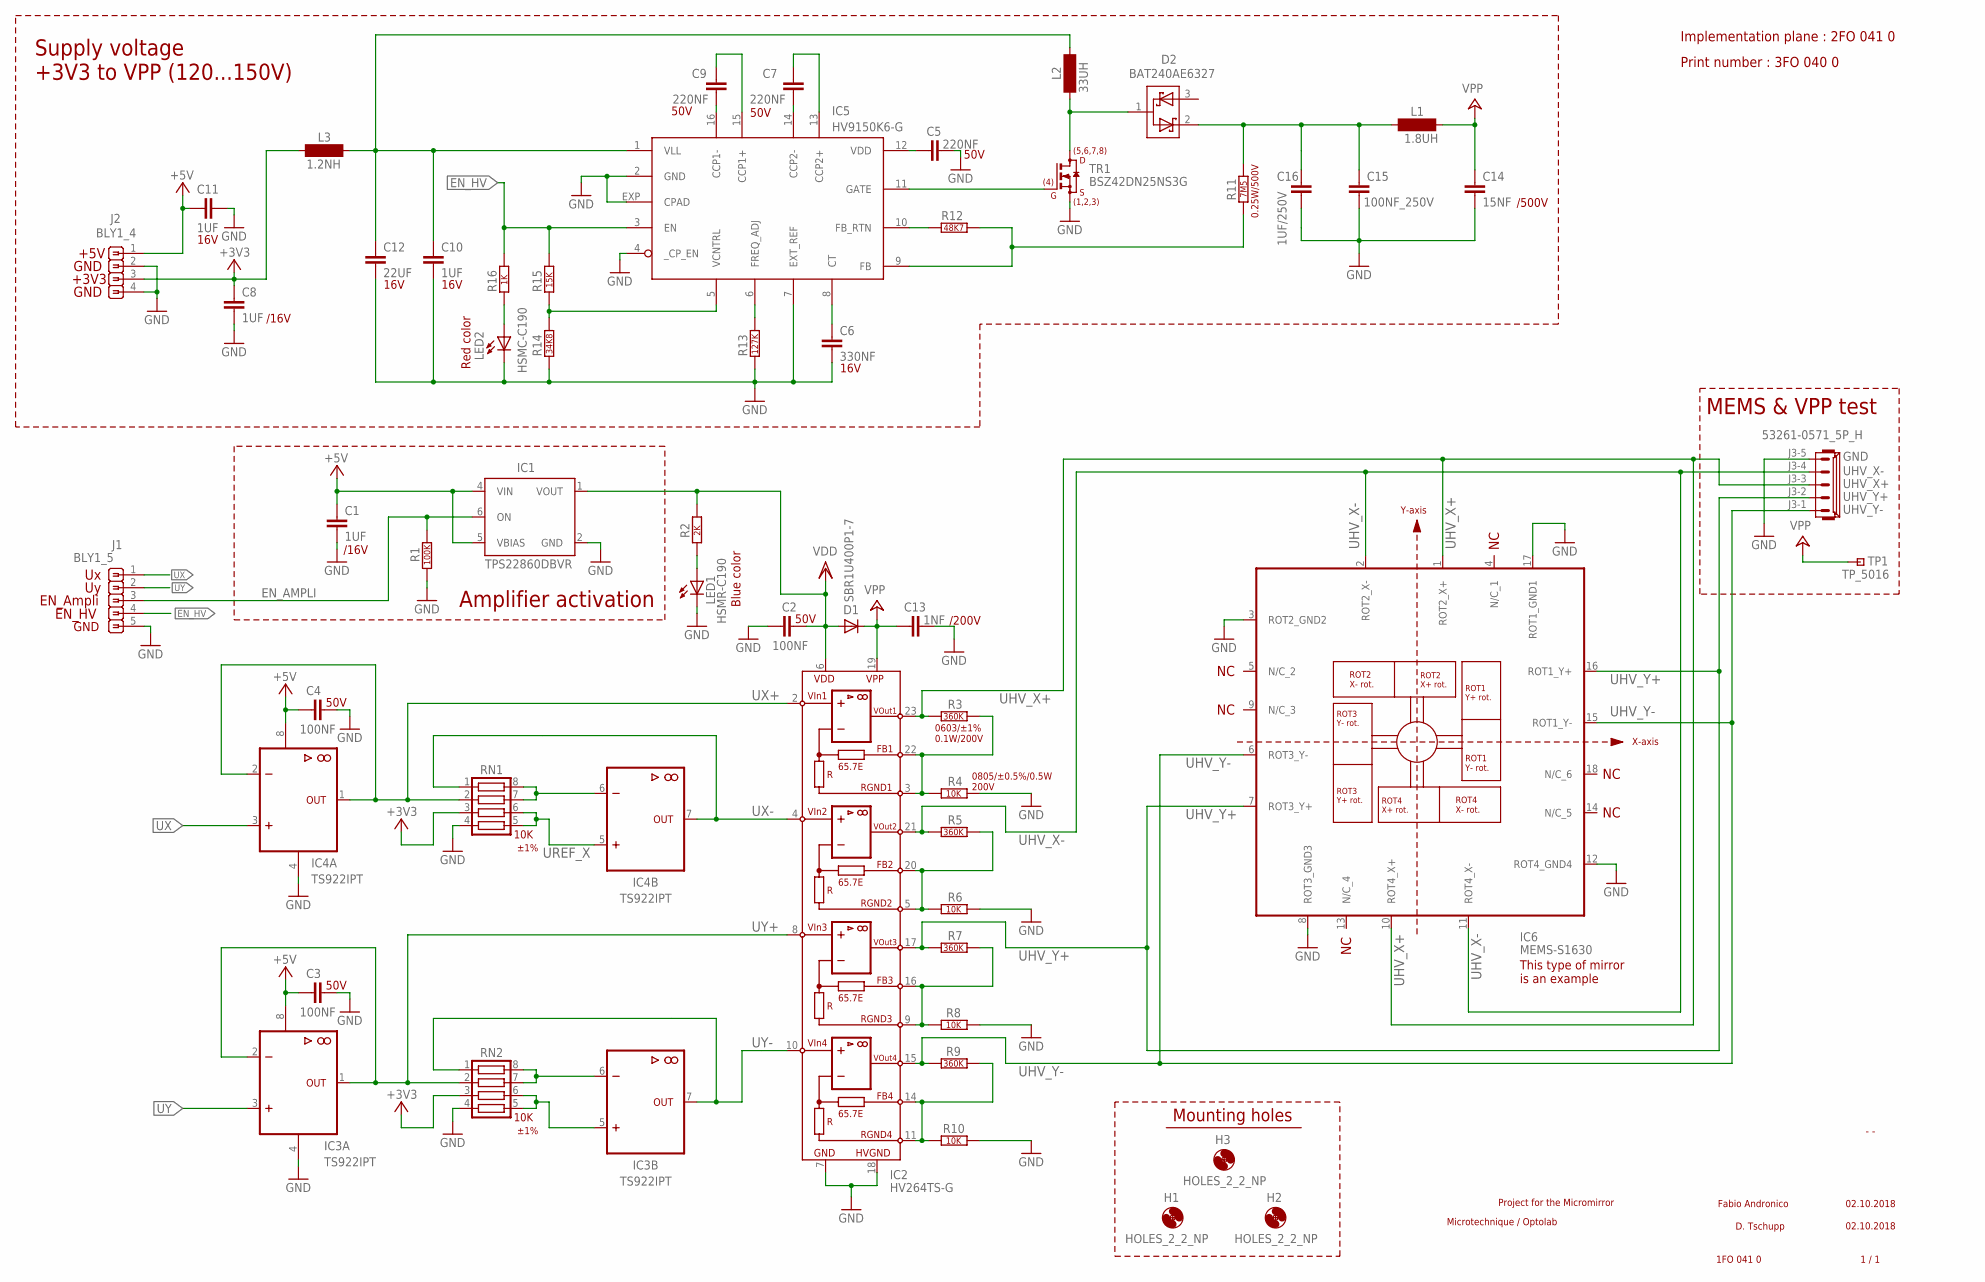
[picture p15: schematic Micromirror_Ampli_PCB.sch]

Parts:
C1, C8, C10, C11: 1UF; C0603
C2, C3, C4: 100NF; C0603
C5, C7, C9: 220NF; C0603
C6: 330NF; C0603
C12: 22UF; C0805
C13: 1NF; C0603
C14: 15NF; C0805
C15: 100NF_250V; C0805
C16: 1UF/250V; C1812
D1: SBR1U400P1-7; POWERDI_123
D2: BAT240AE6327; SOT23-3
H1, H2, H3: HOLES_2_2_NP; 2_2_NP
IC1: TPS22860DBVR; SOT23-6
IC2: HV264TS-G; TSSOP24
IC3, IC4: TS922IPT; TSSOP8
IC5: HV9150K6-G; QFN16
IC6: MEMS-S1630; LCC18
J1: BLY1_5; BLY1_5_2MM
J2: BLY1_4; BLY1_4_2MM
J3: 53261-0571_5P_H; 53261-05
L1: 1.8UH; L0805
L2: 33UH; NR5040
L3: 1.2NH; L08051R2CEWTR
LED1: HSMR-C190; CHIP-LED-0603
LED2: HSMC-C190; CHIP-LED-0603
R1: 100K; R0603
R2: 2K; R0603
R3, R5, R7, R9: 360K; R0603
R4, R6, R8, R10: 10K_0.5%; R0805
R11: 7M5; R1206
R12: 48K7; R0603
R13: 127K; R0603
R14: 34K8; R0603
R15: 15K; R0603
R16: 1K_0.1W; R0603
RN1, RN2: 10K; RN1206
TP1: TP_5016; 5016
TR1: BSZ42DN25NS3G; TSDSON-8

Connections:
+3V3: C8.1, J2.3, L3.1, RN1.3, RN2.3
+5V: C1.1, C3.1, C4.1, C11.1, IC1.4 (VIN), IC1.5 (VBIAS), IC3.8 (+5V), IC4.8 (+5V), J2.1
EN_AMPLI: IC1.6 (ON), J1.3, R1.1
EN_HV: IC5.3 (EN), J1.4, R15.2, R16.2
GND: C1.2, C2.2, C3.2, C4.2, C5.1, C6.2, C8.2, C10.2, C11.2, C12.2, C13.2, C14.2, C15.2, C16.2, IC1.2 (GND), IC2.7 (GND), IC2.18 (HVGND), IC3.4 (GND), IC4.4 (GND), IC5.2 (GND), IC5.4 (_CP_EN), IC5.7 (EXT_REF), IC5.EXP (CPAD), IC6.3 (ROT2_GND2), IC6.8 (ROT3_GND3), IC6.12 (ROT4_GND4), IC6.17 (ROT1_GND1), J1.5, J2.2, J2.4, J3.5, LED1.C, LED2.C, R1.2, R4.2, R6.2, R8.2, R10.2, R13.1, R14.1, RN1.4, RN2.4, TR1.1 (S), TR1.2 (S), TR1.3 (S)
unnamed: IC5.11 (GATE), TR1.4 (G)
unnamed: C9.1, IC5.16 (CCP1-)
unnamed: C9.2, IC5.15 (CCP1+)
unnamed: C7.2, IC5.14 (CCP2-)
unnamed: C7.1, IC5.13 (CCP2+)
unnamed: C5.2, IC5.12 (VDD)
unnamed: IC5.5 (VCNTRL), R14.2, R15.1
unnamed: IC5.6 (FREQ_ADJ), R13.2
unnamed: C6.1, IC5.8 (CT)
unnamed: D2.1, L2.1, TR1.5 (D)
unnamed: IC5.10 (FB_RTN), R12.1
unnamed: C15.1, C16.1, D2.2, L1.1, R11.2
unnamed: IC5.9 (FB), R11.1, R12.2
unnamed: IC3.6 (-IN), RN2.7, RN2.8
unnamed: IC3.5 (+IN), RN2.5, RN2.6
unnamed: LED2.A, R16.1
unnamed: IC2.3 (RGND1), IC2.22 (FB1), R3.2, R4.1
unnamed: IC4.6 (-IN), RN1.7, RN1.8
unnamed: IC2.5 (RGND2), IC2.20 (FB2), R5.2, R6.1
unnamed: LED1.A, R2.1
unnamed: C10.1, C12.1, IC5.1 (VLL), L2.2, L3.2
unnamed: IC2.9 (RGND3), IC2.16 (FB3), R7.2, R8.1
unnamed: IC2.11 (RGND4), IC2.14 (FB4), R9.2, R10.1
UHV_X+: IC2.23 (VOUT1), IC6.1 (ROT2_X+), IC6.10 (ROT4_X+), J3.3, R3.1
UHV_X-: IC2.21 (VOUT2), IC6.2 (ROT2_X-), IC6.11 (ROT4_X-), J3.4, R5.1
UHV_Y+: IC2.17 (VOUT3), IC6.7 (ROT3_Y+), IC6.16 (ROT1_Y+), J3.2, R7.1
UHV_Y-: IC2.15 (VOUT4), IC6.6 (ROT3_Y-), IC6.15 (ROT1_Y-), J3.1, R9.1
UREF_X: IC4.5 (+IN), RN1.5, RN1.6
UX: IC4.3 (+IN), J1.1
UX+: IC2.2 (+VIN1), IC4.1 (OUT), IC4.2 (-IN), RN1.2
UX-: IC2.4 (+VIN2), IC4.7 (OUT), RN1.1
UY: IC3.3 (+IN), J1.2
UY+: IC2.8 (+VIN3), IC3.1 (OUT), IC3.2 (-IN), RN2.2
UY-: IC2.10 (+VIN4), IC3.7 (OUT), RN2.1
VDD: C2.1, D1.A, IC1.1 (VOUT), IC2.6 (VDD), R2.2
VPP: C13.1, C14.1, D1.C, IC2.19 (VPP), L1.2, TP1.1

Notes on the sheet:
Fabio Andronico
02.10.2018
1FO 041 0
1 / 1
- -
Microtechnique / Optolab
Project for the Micromirror
D. Tschupp
Print number : 3FO 040 0
Implementation plane : 2FO 041 0
+5V
GND
+3V3
EN_HV
EN_Ampli
Supply voltage +3V3 to VPP (120...150V)
Amplifier activation
MEMS & VPP test
Mounting holes
0603/±1% 0.1W/200V
0805/±0.5%/0.5W 200V
0.25W/500V
Blue color
Red color
/200V
/500V
This type of mirror is an example
±1%
/16V
16V
50V

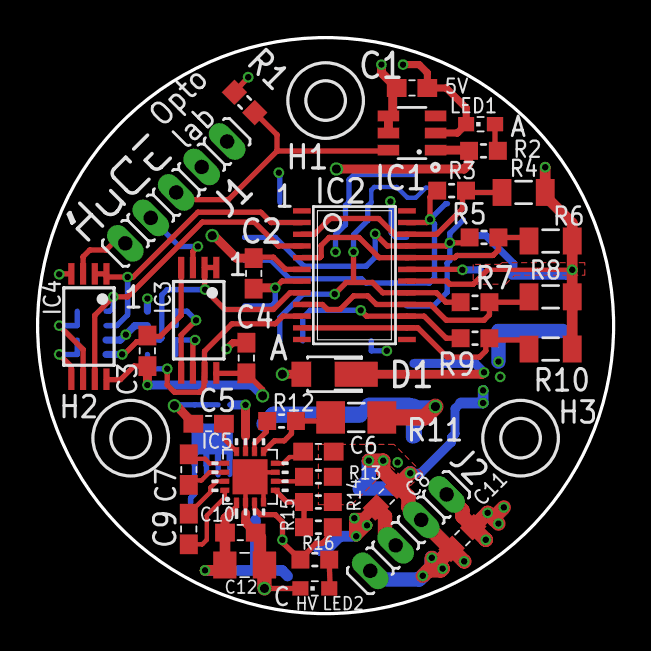
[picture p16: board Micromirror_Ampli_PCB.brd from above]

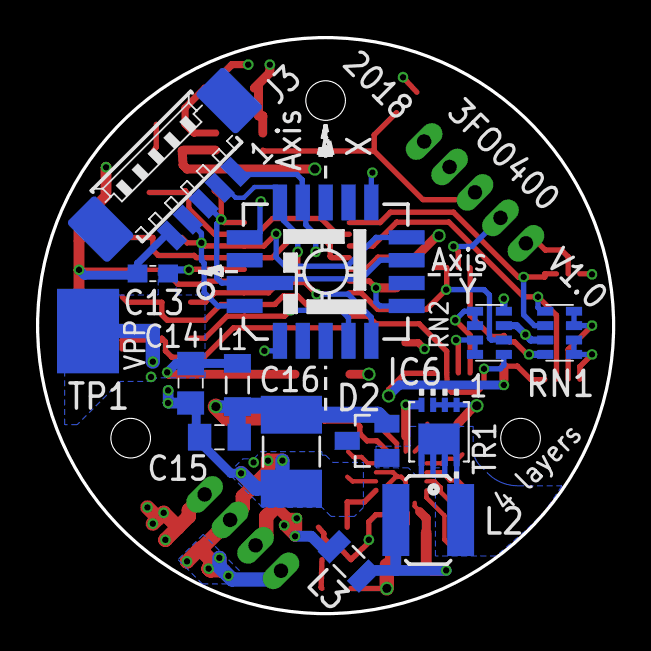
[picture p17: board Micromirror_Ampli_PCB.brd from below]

Board: 4 copper layers, 32.0 x 32.0 mm, 66 parts (14 on the bottom side), 41 nets.

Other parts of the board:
DRILEGEND: DRILEGEND
U$2: DIN_A4_L_LOC_LAYER_TOP
U$3: DIN_A4_L_LOC_INNERLAYER2
U$4: DIN_A4_L_LOC_SILKSCREEN_TOP
U$5: DIN_A4_L_LOC_LAYER_BOTTOM
U$6: DIN_A4_L_LOC_SILKSCREEN_BOTTOM
U$7: DIN_A4_L_LOC_INNERLAYER3
U$8: DIN_A4_L_LOC_DRILL_BFH
U$9: COUPE_4L_1,6
U$10: DIN_A4_L_LOC_TOP_DOCU
U$11: DIN_A4_L_LOC_BOTTOM_DOCU

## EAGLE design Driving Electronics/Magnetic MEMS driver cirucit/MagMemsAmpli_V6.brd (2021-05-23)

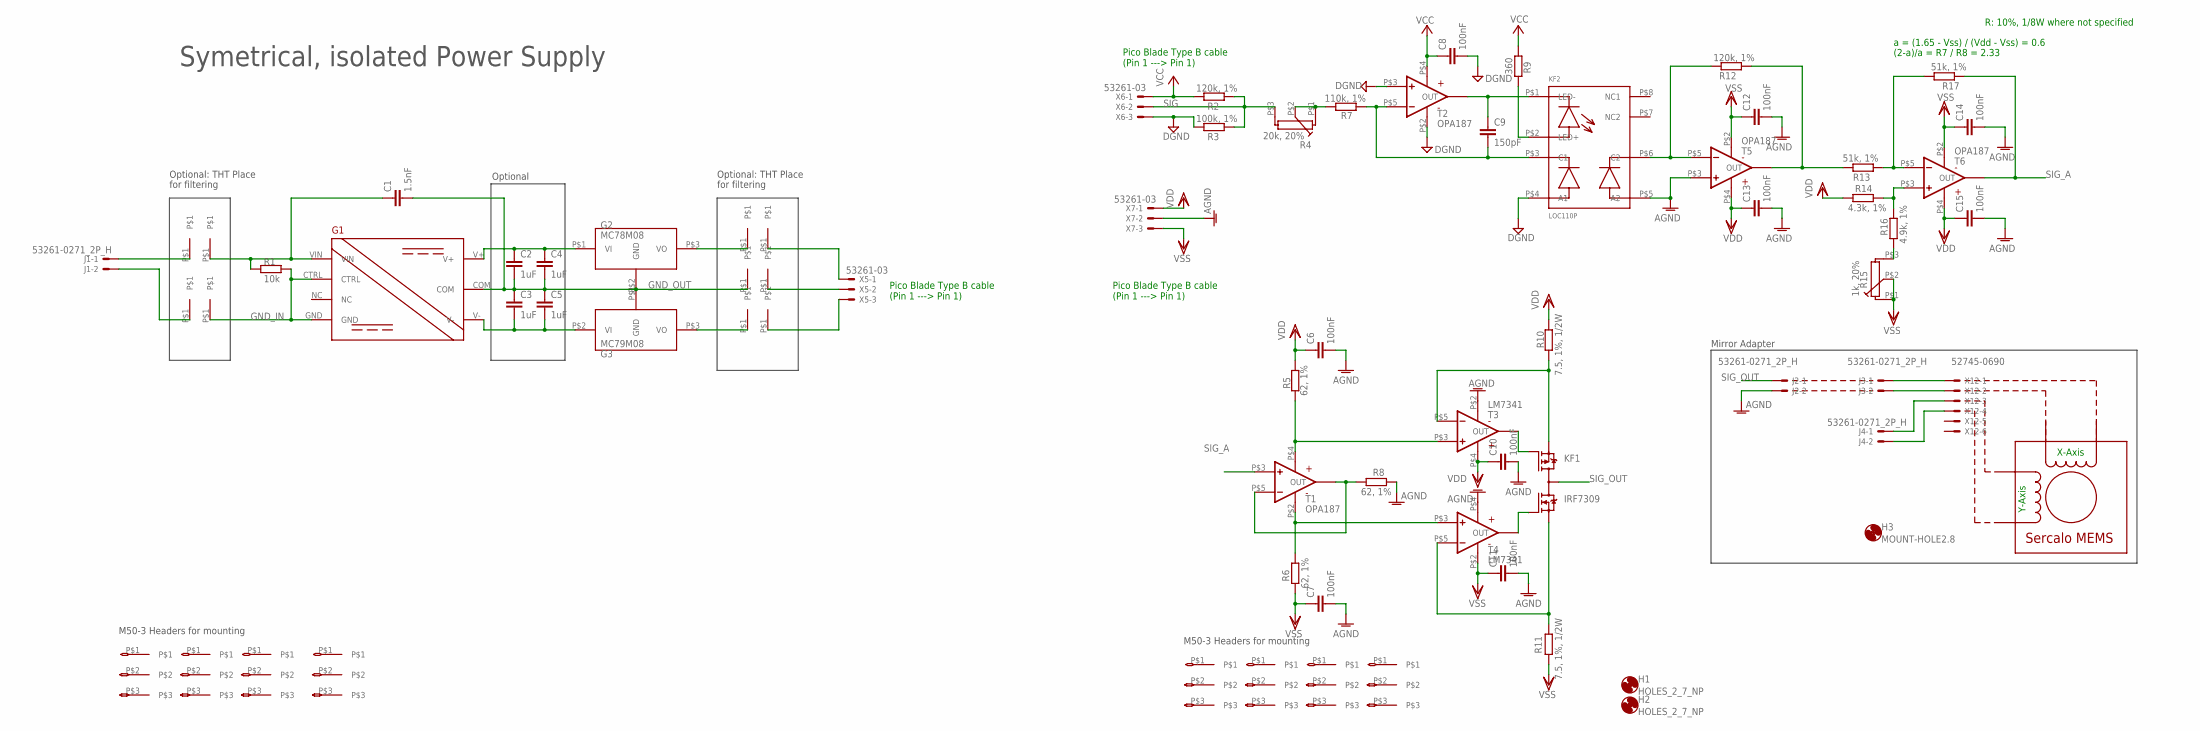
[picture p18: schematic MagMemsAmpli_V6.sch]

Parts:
C1: 1.5nF; C0805K; MOUSER 0805B152K500CT
C2, C3, C4, C5: 1uF; C0805K; MOUSER 0805B105K500CT
C6, C7, C8, C10, C11, C12, C13, C14, C15: 100nF; C0603K; MOUSER 06033C104KAT4A
C9: 150pF; C0603K; MOUSER C0603C101M5HACTU
G1: RS6-0512D; RS_THT
G2: MC78M08; DPAK-3; MOUSER MC78M08CDTG
G3: MC79M08; DPAK-3
H1, H2: HOLES_2_7_NP; 2_7_NP
H3: MOUNT-HOLE2.8; 2,8
J1, J2, J3, J4: 53261-0271_2P_H; 53261-02
KF1: IRF7309; SO08-IRF
KF2: LOC110P
R1: 10k; R0603; MOUSER ESR03EZPF62R0
R2, R12: 120k, 1%; R0603; MOUSER MCT06030C1203FP500
R3: 100k, 1%; R0603; MOUSER MCT06030C1003FP500
R4: 20k, 20%; SM-3T; MOUSER SM-3TW203
R5, R6, R8: 62, 1%; R0603; MOUSER ESR03EZPF62R0
R7: 110k, 1%; R0603; MOUSER CRCW0603110KFKEAC
R9: 360; R0603; MOUSER MR06X3600FTL
R10, R11: 7.5, 1%, 1/2W; R0805; MOUSER ESR10EZPF7R50
R13, R17: 51k, 1%; R0603; MOUSER MCT06030C5102FP500
R14: 4.3k, 1%; R0603; MOUSER SDR03EZPF4301
R15: 1k, 20%; SM-3T; MOUSER SM-3TW102
R16: 4.9k, 1%; R0603; MOUSER MCT0603MC4701FP500
T1, T2, T5, T6: OPA187; SOT23-5
T3, T4: LM7341; SOT23-5
TP1, TP2, TP3, TP4, TP5, TP6, TP7, TP8, TP9, TP10: TP10
X1, X2, X3, X4: M50-3; MOUSER M50-3030342
X5, X6, X7: 53261-03; MOUSER 53261-0371
X8, X9, X10, X11: M50-3; MOUSER M50-3530342
X12: 52745-0690; MOUSER 52745-0697

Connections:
AGND: C6.2, C7.2, C10.2, C11.2, C12.2, C13.2, C14.2, C15.2, J2.2, KF2.P$5 (A2), R8.1, T3.P$2 (V-), T4.P$4 (V+), T5.P$3 (+IN), X7.2
DGND: C8.2, KF2.P$4 (A1), R3.2, T2.P$2 (V-), T2.P$3 (+IN), X6.3
GND_IN: G1.CTRL, G1.GND, R1.2, TP4.P$1
GND_OUT: C1.2, C2.2, C3.1, C4.2, C5.1, G1.COM, G2.P$2 (GND), G3.P$1 (GND), TP6.P$1
unnamed: C1.1, G1.VIN, R1.1, TP3.P$1
unnamed: C2.1, C4.1, G1.V+, G2.P$1 (VI)
unnamed: C3.2, C5.2, G1.V-, G3.P$2 (VI)
unnamed: J1.1, TP1.P$1
unnamed: J1.2, TP2.P$1
unnamed: C9.1, KF2.P$1 (LED-), T2.P$1 (OUT)
unnamed: KF2.P$2 (LED+), R9.1
unnamed: R13.1, R17.2, T6.P$5 (-IN)
unnamed: R12.1, R13.2, T5.P$1 (OUT)
unnamed: C9.2, KF2.P$3 (C1), R7.2, T2.P$5 (-IN)
unnamed: KF2.P$6 (C2), R12.2, T5.P$5 (-IN)
unnamed: R14.2, R16.2, T6.P$3 (+IN)
unnamed: G2.P$3 (VO), TP5.P$1
unnamed: G3.P$3 (VO), TP7.P$1
unnamed: TP8.P$1, X5.1
unnamed: TP9.P$1, X5.2
unnamed: TP10.P$1, X5.3
unnamed: KF1.3 (P-S), R10.1, T3.P$5 (-IN)
unnamed: KF1.4 (P-G), T3.P$1 (OUT)
unnamed: KF1.2 (N-G), T4.P$1 (OUT)
unnamed: KF1.1 (N-S), R11.2, T4.P$5 (-IN)
unnamed: R8.2, T1.P$1 (OUT), T1.P$5 (-IN)
unnamed: R6.2, T1.P$2 (V-), T4.P$3 (+IN)
unnamed: R5.1, T1.P$4 (V+), T3.P$3 (+IN)
unnamed: J3.1, X12.1
unnamed: J3.2, X12.2
unnamed: J4.1, X12.3
unnamed: J4.2, X12.4
unnamed: R4.P$1 (1A), R4.P$2 (1S), R7.1
unnamed: R15.P$3 (1E), R16.1
SIG: R2.1, R3.1, R4.P$3 (1E), X6.2
SIG_A: R17.1, T1.P$3 (+IN), T6.P$1 (OUT)
SIG_OUT: J2.1, KF1.5 (D), KF1.6 (D), KF1.7 (D), KF1.8 (D)
VCC: C8.1, R2.2, R9.2, T2.P$4 (V+), X6.1
VDD: C6.1, C10.1, C13.1, C15.1, R5.2, R10.2, R14.1, T3.P$4 (V+), T5.P$4 (V+), T6.P$4 (V+), X7.1
VSS: C7.1, C11.1, C12.1, C14.1, R6.1, R11.1, R15.P$1 (1A), R15.P$2 (1S), T4.P$2 (V-), T5.P$2 (V-), T6.P$2 (V-), X7.3

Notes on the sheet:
(2-a)/a = R7 / R8 = 2.33
X-Axis
Y-Axis
R: 10%, 1/8W where not specified
Pico Blade Type B cable (Pin 1 ---> Pin 1)
Optional
Optional: THT Place
for filtering
M50-3 Headers for mounting
Mirror Adapter
Symetrical, isolated Power Supply
a = (1.65 - Vss) / (Vdd - Vss) = 0.6

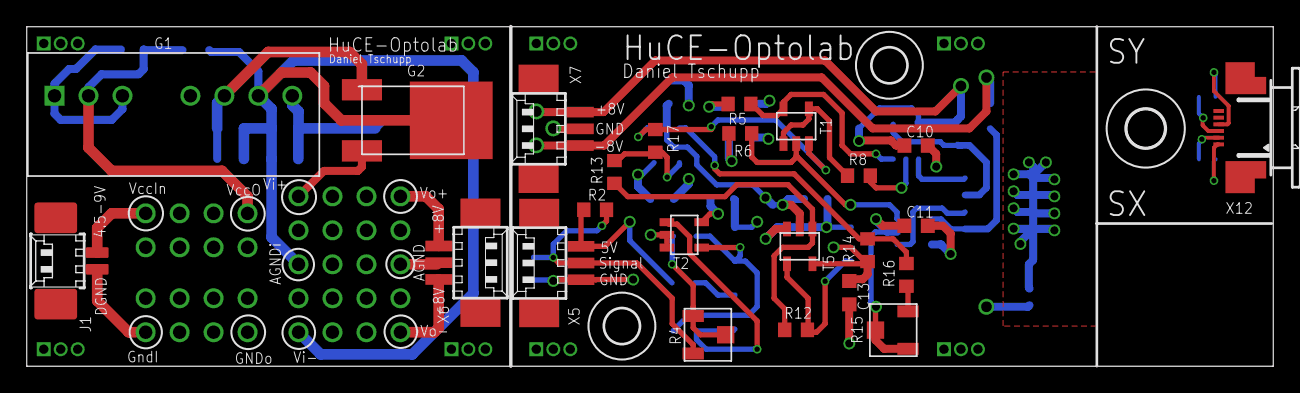
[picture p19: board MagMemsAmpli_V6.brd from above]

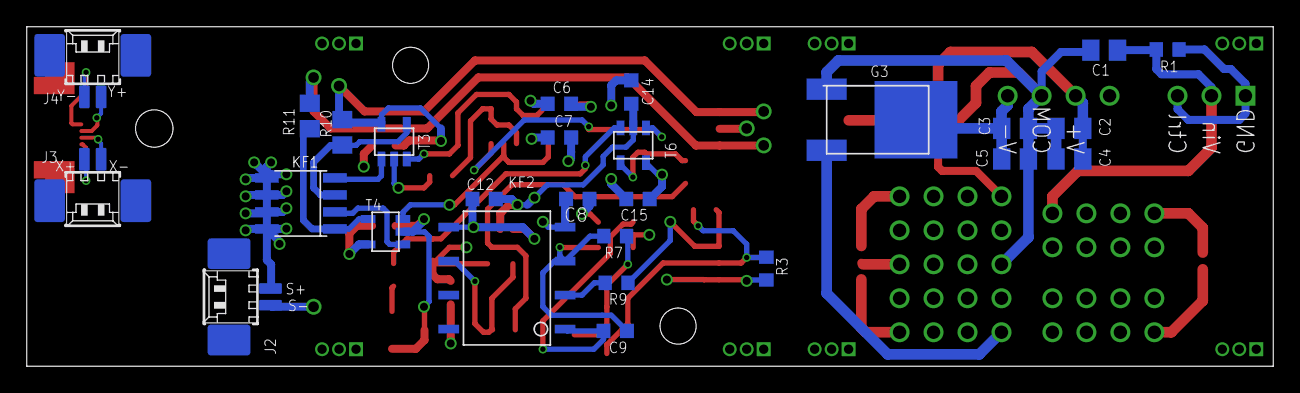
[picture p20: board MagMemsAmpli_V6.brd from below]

Board: 4 copper layers, 93.2 x 25.4 mm, 72 parts (27 on the bottom side), 40 nets.

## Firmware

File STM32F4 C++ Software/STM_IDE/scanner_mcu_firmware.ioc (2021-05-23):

#MicroXplorer Configuration settings - do not modify
DAC.DAC_OutputBuffer=DAC_OUTPUTBUFFER_ENABLE
DAC.DAC_OutputBuffer2=DAC_OUTPUTBUFFER_ENABLE
DAC.DAC_Trigger=DAC_TRIGGER_NONE
DAC.DAC_Trigger2=DAC_TRIGGER_NONE
DAC.IPParameters=DAC_Trigger,DAC_Trigger2,DAC_OutputBuffer,DAC_OutputBuffer2
File.Version=6
GPIO.groupedBy=Group By Peripherals
KeepUserPlacement=false
Mcu.Family=STM32F4
Mcu.IP0=DAC
Mcu.IP1=NVIC
Mcu.IP2=RCC
Mcu.IP3=SYS
Mcu.IP4=TIM1
Mcu.IP5=TIM3
Mcu.IP6=TIM13
Mcu.IP7=TIM14
Mcu.IP8=USART2
Mcu.IP9=USART3
Mcu.IPNb=10
Mcu.Name=STM32F405RGTx
Mcu.Package=LQFP64
Mcu.Pin0=PH0-OSC_IN
Mcu.Pin1=PH1-OSC_OUT
Mcu.Pin10=PA13
Mcu.Pin11=PA14
Mcu.Pin12=PC10
Mcu.Pin13=PC11
Mcu.Pin14=PC12
Mcu.Pin15=PB3
Mcu.Pin16=VP_SYS_VS_Systick
Mcu.Pin17=VP_TIM1_VS_ClockSourceINT
Mcu.Pin18=VP_TIM1_VS_no_output3
Mcu.Pin19=VP_TIM3_VS_no_output4
Mcu.Pin2=PA0-WKUP
Mcu.Pin20=VP_TIM13_VS_ClockSourceINT
Mcu.Pin21=VP_TIM14_VS_ClockSourceINT
Mcu.Pin3=PA2
Mcu.Pin4=PA3
Mcu.Pin5=PA4
Mcu.Pin6=PA5
Mcu.Pin7=PB0
Mcu.Pin8=PB11
Mcu.Pin9=PA9
Mcu.PinsNb=22
Mcu.ThirdPartyNb=0
Mcu.UserConstants=
Mcu.UserName=STM32F405RGTx
MxCube.Version=4.26.1
MxDb.Version=DB.4.0.261
NVIC.BusFault_IRQn=true\:0\:0\:false\:false\:true\:false\:false
NVIC.DebugMonitor_IRQn=true\:0\:0\:false\:false\:true\:false\:false
NVIC.ForceEnableDMAVector=true
NVIC.HardFault_IRQn=true\:0\:0\:false\:false\:true\:false\:false
NVIC.MemoryManagement_IRQn=true\:0\:0\:false\:false\:true\:false\:false
NVIC.NonMaskableInt_IRQn=true\:0\:0\:false\:false\:true\:false\:false
NVIC.PendSV_IRQn=true\:0\:0\:false\:false\:true\:false\:false
NVIC.PriorityGroup=NVIC_PRIORITYGROUP_4
NVIC.SVCall_IRQn=true\:0\:0\:false\:false\:true\:false\:false
NVIC.SysTick_IRQn=true\:0\:0\:false\:false\:true\:false\:true
NVIC.TIM1_CC_IRQn=true\:0\:0\:false\:false\:true\:true\:true
NVIC.TIM3_IRQn=true\:0\:0\:false\:false\:true\:true\:true
NVIC.TIM8_TRG_COM_TIM14_IRQn=true\:0\:0\:false\:false\:true\:true\:true
NVIC.TIM8_UP_TIM13_IRQn=true\:0\:0\:false\:false\:true\:true\:true
NVIC.USART2_IRQn=true\:0\:0\:false\:false\:true\:true\:true
NVIC.USART3_IRQn=true\:0\:0\:false\:false\:true\:true\:true
NVIC.UsageFault_IRQn=true\:0\:0\:false\:false\:true\:false\:false
PA0-WKUP.GPIOParameters=GPIO_PuPd
PA0-WKUP.GPIO_PuPd=GPIO_PULLDOWN
PA0-WKUP.Locked=true
PA0-WKUP.Signal=GPIO_Output
PA13.Mode=Trace_Asynchronous_SW
PA13.Signal=SYS_JTMS-SWDIO
PA14.Mode=Trace_Asynchronous_SW
PA14.Signal=SYS_JTCK-SWCLK
PA2.Mode=Asynchronous
PA2.Signal=USART2_TX
PA3.Mode=Asynchronous
PA3.Signal=USART2_RX
PA4.GPIOParameters=GPIO_Label
PA4.GPIO_Label=DAC_OUT1_UX
PA4.Signal=COMP_DAC1_group
PA5.GPIOParameters=GPIO_Label
PA5.GPIO_Label=DAC_OUT2_UY
PA5.Signal=COMP_DAC2_group
PA9.Locked=true
PA9.Signal=S_TIM1_CH2
PB0.Locked=true
PB0.Signal=S_TIM3_CH3
PB11.Mode=Asynchronous
PB11.Signal=USART3_RX
PB3.Mode=Trace_Asynchronous_SW
PB3.Signal=SYS_JTDO-SWO
PC10.Mode=Asynchronous
PC10.Signal=USART3_TX
PC11.GPIOParameters=GPIO_Label
PC11.GPIO_Label=CBUS3
PC11.Locked=true
PC11.Signal=GPIO_Output
PC12.GPIOParameters=GPIO_Label
PC12.GPIO_Label=CBUS0
PC12.Locked=true
PC12.Signal=GPIO_Output
PH0-OSC_IN.Mode=HSE-External-Oscillator
PH0-OSC_IN.Signal=RCC_OSC_IN
PH1-OSC_OUT.Mode=HSE-External-Oscillator
PH1-OSC_OUT.Signal=RCC_OSC_OUT
PinOutPanel.RotationAngle=0
ProjectManager.AskForMigrate=false
ProjectManager.BackupPrevious=false
ProjectManager.CompilerOptimize=6
ProjectManager.ComputerToolchain=false
ProjectManager.CoupleFile=true
ProjectManager.CustomerFirmwarePackage=
ProjectManager.DefaultFWLocation=true
ProjectManager.DeletePrevious=true
ProjectManager.DeviceId=STM32F405RGTx
ProjectManager.FirmwarePackage=STM32Cube FW_F4 V1.21.0
ProjectManager.FreePins=true
ProjectManager.HalAssertFull=false
ProjectManager.HeapSize=0x1200
ProjectManager.KeepUserCode=true
ProjectManager.LastFirmware=true
ProjectManager.LibraryCopy=1
ProjectManager.MainLocation=Core/Src
ProjectManager.NoMain=false
ProjectManager.PreviousToolchain=STM32CubeIDE
ProjectManager.ProjectBuild=false
ProjectManager.ProjectFileName=scanner_mcu_firmware.ioc
ProjectManager.ProjectName=scanner_mcu_firmware
ProjectManager.StackSize=0x1200
ProjectManager.TargetToolchain=STM32CubeIDE
ProjectManager.ToolChainLocation=
ProjectManager.UnderRoot=true
ProjectManager.functionlistsort=1-MX_GPIO_Init-GPIO-false-HAL-true,2-SystemClock_Config-RCC-false-HAL-false,3-MX_DAC_Init-DAC-false-HAL-true,4-MX_TIM13_Init-TIM13-false-HAL-true,5-MX_TIM1_Init-TIM1-false-HAL-true,6-MX_TIM14_Init-TIM14-false-HAL-true,7-MX_USART3_UART_Init-USART3-false-HAL-true,8-MX_TIM3_Init-TIM3-false-HAL-true,9-MX_USART2_UART_Init-USART2-false-HAL-true
RCC.48MHZClocksFreq_Value=67200000
RCC.AHBFreq_Value=168000000
RCC.APB1CLKDivider=RCC_HCLK_DIV4
RCC.APB1Freq_Value=42000000
RCC.APB1TimFreq_Value=84000000
RCC.APB2CLKDivider=RCC_HCLK_DIV2
RCC.APB2Freq_Value=84000000
RCC.APB2TimFreq_Value=168000000
RCC.CortexFreq_Value=168000000
RCC.EthernetFreq_Value=168000000
RCC.FCLKCortexFreq_Value=168000000
RCC.FamilyName=M
RCC.HCLKFreq_Value=168000000
RCC.HSE_VALUE=8000000
RCC.HSI_VALUE=16000000
RCC.I2SClocksFreq_Value=192000000
RCC.IPParameters=48MHZClocksFreq_Value,AHBFreq_Value,APB1CLKDivider,APB1Freq_Value,APB1TimFreq_Value,APB2CLKDivider,APB2Freq_Value,APB2TimFreq_Value,CortexFreq_Value,EthernetFreq_Value,FCLKCortexFreq_Value,FamilyName,HCLKFreq_Value,HSE_VALUE,HSI_VALUE,I2SClocksFreq_Value,LSE_VALUE,LSI_VALUE,MCO2PinFreq_Value,PLLCLKFreq_Value,PLLM,PLLN,PLLQ,PLLQCLKFreq_Value,PLLSourceVirtual,RTCFreq_Value,RTCHSEDivFreq_Value,SYSCLKFreq_VALUE,SYSCLKSource,VCOI2SOutputFreq_Value,VCOInputFreq_Value,VCOOutputFreq_Value,VcooutputI2S
RCC.LSE_VALUE=32768
RCC.LSI_VALUE=32000
RCC.MCO2PinFreq_Value=168000000
RCC.PLLCLKFreq_Value=168000000
RCC.PLLM=4
RCC.PLLN=168
RCC.PLLQ=5
RCC.PLLQCLKFreq_Value=67200000
RCC.PLLSourceVirtual=RCC_PLLSOURCE_HSE
RCC.RTCFreq_Value=32000
RCC.RTCHSEDivFreq_Value=4000000
RCC.SYSCLKFreq_VALUE=168000000
RCC.SYSCLKSource=RCC_SYSCLKSOURCE_PLLCLK
RCC.VCOI2SOutputFreq_Value=384000000
RCC.VCOInputFreq_Value=2000000
RCC.VCOOutputFreq_Value=336000000
RCC.VcooutputI2S=192000000
SH.COMP_DAC1_group.0=DAC_OUT1,DAC_OUT1
SH.COMP_DAC1_group.ConfNb=1
SH.COMP_DAC2_group.0=DAC_OUT2,DAC_OUT2
SH.COMP_DAC2_group.ConfNb=1
SH.S_TIM1_CH2.0=TIM1_CH2,PWM Generation2 CH2
SH.S_TIM1_CH2.ConfNb=1
SH.S_TIM3_CH3.0=TIM3_CH3,PWM Generation3 CH3
SH.S_TIM3_CH3.ConfNb=1
TIM1.Channel-Output\ Compare2\ CH2\ CH2N=TIM_CHANNEL_2
TIM1.Channel-Output\ Compare3\ No\ Output=TIM_CHANNEL_3
TIM1.Channel-PWM\ Generation2\ CH2=TIM_CHANNEL_2
TIM1.IPParameters=Prescaler,Period,Channel-Output Compare3 No Output,Channel-PWM Generation2 CH2,Channel-Output Compare2 CH2 CH2N,Pulse-PWM Generation2 CH2
TIM1.Period=100
TIM1.Prescaler=1
TIM1.Pulse-PWM\ Generation2\ CH2=50
TIM13.IPParameters=Prescaler,Period
TIM13.Period=2100-1
TIM13.Prescaler=1
TIM14.IPParameters=Prescaler,Period
TIM14.Period=200-1
TIM14.Prescaler=42000
TIM3.Channel-Output\ Compare4\ No\ Output=TIM_CHANNEL_4
TIM3.Channel-PWM\ Generation3\ CH3=TIM_CHANNEL_3
TIM3.IPParameters=Channel-Output Compare4 No Output,Prescaler,Period,Channel-PWM Generation3 CH3,Pulse-PWM Generation3 CH3
TIM3.Period=100
TIM3.Prescaler=1
TIM3.Pulse-PWM\ Generation3\ CH3=50
USART2.IPParameters=VirtualMode
USART2.VirtualMode=VM_ASYNC
USART3.IPParameters=VirtualMode
USART3.VirtualMode=VM_ASYNC
VP_SYS_VS_Systick.Mode=SysTick
VP_SYS_VS_Systick.Signal=SYS_VS_Systick
VP_TIM13_VS_ClockSourceINT.Mode=Enable_Timer
VP_TIM13_VS_ClockSourceINT.Signal=TIM13_VS_ClockSourceINT
VP_TIM14_VS_ClockSourceINT.Mode=Enable_Timer
VP_TIM14_VS_ClockSourceINT.Signal=TIM14_VS_ClockSourceINT
VP_TIM1_VS_ClockSourceINT.Mode=Internal
VP_TIM1_VS_ClockSourceINT.Signal=TIM1_VS_ClockSourceINT
VP_TIM1_VS_no_output3.Mode=Output Compare3 No Output
VP_TIM1_VS_no_output3.Signal=TIM1_VS_no_output3
VP_TIM3_VS_no_output4.Mode=Output Compare4 No Output
VP_TIM3_VS_no_output4.Signal=TIM3_VS_no_output4
board=custom
isbadioc=false

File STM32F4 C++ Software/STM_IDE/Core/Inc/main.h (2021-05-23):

/**
  ******************************************************************************
  * @file           : main.h
  * @brief          : Header for main.c file.
  *                   This file contains the common defines of the application.
  ******************************************************************************
  ** This notice applies to any and all portions of this file
  * that are not between comment pairs USER CODE BEGIN and
  * USER CODE END. Other portions of this file, whether 
  * inserted by the user or by software development tools
  * are owned by their respective copyright owners.
  *
  * COPYRIGHT(c) 2020 STMicroelectronics
  *
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
  ******************************************************************************
  */

/* Define to prevent recursive inclusion -------------------------------------*/
#ifndef __MAIN_H__
#define __MAIN_H__

/* Includes ------------------------------------------------------------------*/

/* USER CODE BEGIN Includes */

/* USER CODE END Includes */

/* Private define ------------------------------------------------------------*/

#define DAC_OUT1_UX_Pin GPIO_PIN_4
#define DAC_OUT1_UX_GPIO_Port GPIOA
#define DAC_OUT2_UY_Pin GPIO_PIN_5
#define DAC_OUT2_UY_GPIO_Port GPIOA
#define CBUS3_Pin GPIO_PIN_11
#define CBUS3_GPIO_Port GPIOC
#define CBUS0_Pin GPIO_PIN_12
#define CBUS0_GPIO_Port GPIOC

/* ########################## Assert Selection ############################## */
/**
  * @brief Uncomment the line below to expanse the "assert_param" macro in the 
  *        HAL drivers code
  */
/* #define USE_FULL_ASSERT    1U */

/* USER CODE BEGIN Private defines */

/* USER CODE END Private defines */

#ifdef __cplusplus
 extern "C" {
#endif
void _Error_Handler(char *, int);

#define Error_Handler() _Error_Handler(__FILE__, __LINE__)
#ifdef __cplusplus
}
#endif

#endif /* __MAIN_H__ */

/************************ (C) COPYRIGHT STMicroelectronics *****END OF FILE****/
